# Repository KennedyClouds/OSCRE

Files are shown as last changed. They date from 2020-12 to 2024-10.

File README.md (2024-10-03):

## Documentation for the Open Snowflake Camera for Research and Education (OSCRE)

banner

Welcome to OSCRE! This platform is motivated by the need for open, affordable, and upgradeable/adaptable instrumentation to provide microphysical observations for science and educational goals. As the name implies, OSCRE was originally developed to image falling and blowing snow. Components of the system include:
* Machine vision camera + lens
* LED strobe light
* Computer
* Off-the-shelf housings mounted to a DIY wood structure
* 3D-printed parts
* Connecting cables

Within this repository, you will find all of the information needed to purchase parts and build OSCRE.  Example code to obtain images from the camera are also provided. Contributors are welcomed across all fronts ranging from hardware to software. 

## Overview of Components and Specifications

Parts, prices, and links to purchase are provided here: [Google Sheet](https://docs.google.com/spreadsheets/d/e/2PACX-1vRMlBapCWkLHQBSs0PFnScLlecqJcO5ei3qQ1w7xbT3gDOsDzhMCTewoKGWSilK1sk8NCsqLQS7hyFb/pubhtml) As of 3 October 2024, this is out of date and will be updated soon. 

## Camera and Lens

### *Camera*

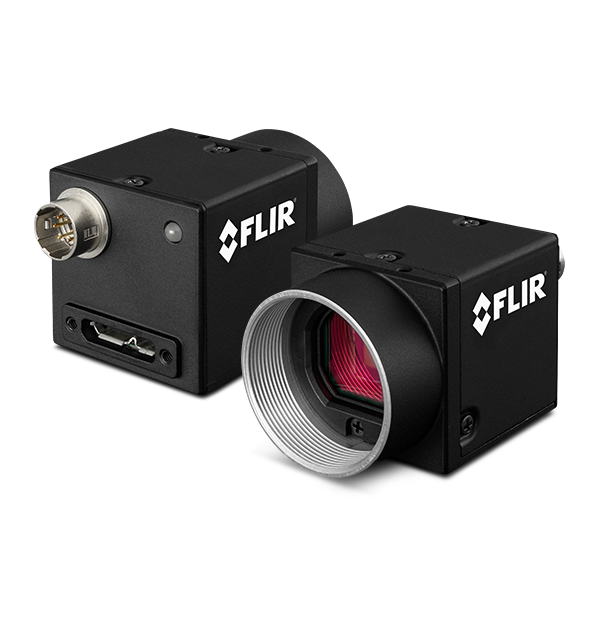
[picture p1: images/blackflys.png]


OSCRE uses a **singular** machine vision camera to obtain images of hydrometeors. These types of cameras are lightweight and rugged, making them ideal for industrial applications such as barcode scanning. A variety of manufacturers exist (Basler, FLIR, JAI, Ximea, etc.) and many of them have models that use identical image sensors from manufacturers such as Sony.

In selecting an appropriate camera/sensor, the following considerations were made:

- Affordability (<$1000 USD)
- Imaging performance (CMOS, monochrome, global shutter, noise performance)
- Minimum exposure time <= 10us (can minimize issues with lighting)
- Adequate General Purpose Input/Output (GPIO) control (this provides the signal to the LED light)
- Software compatibility with ARM architecture (Nvidia GPU computers)
- Adequate frame rate (30+fps)
- Connectivity (USB3)

A quick perusal of any of the manufacturers will yield a mind boggling number of choices. The original testbed used a JAI GO-2400M-USB 2.3MP camera, and this is a perfectly acceptable camera for obtaining images. The downside of this camera is a software SDK free for Windows, but requires an expensive (~$500) computer specific license for other architecture. Supposedly this is changing in 2021, but documentation for the 3rd party SDK is also limited.  

Instead, development shifted to FLIR for the model documented herein. The [FLIR Spinnaker SDK](https://www.flir.com/products/spinnaker-sdk/) is available for all platforms which means you could use any computer you already own to drive the system assuming the hardware is adequate. Based on the criteria above, the Blackfly S line was selected. Balancing the requirements, the [BFS-U3-32S5M-C](https://www.flir.com/products/blackfly-s-usb3/?model=BFS-U3-32S4M-C)  offered the best bang for the buck.  For ~$800, the camera uses the Sony IMX252 monochrome sensor to acquire 3.2MP images at rates up to 118fps. The smaller 1/1.8" sensor is advantageous because it offers a longer focal length for a given resolution, increasing the depth of field compared to larger sensors. 

### *Lens*

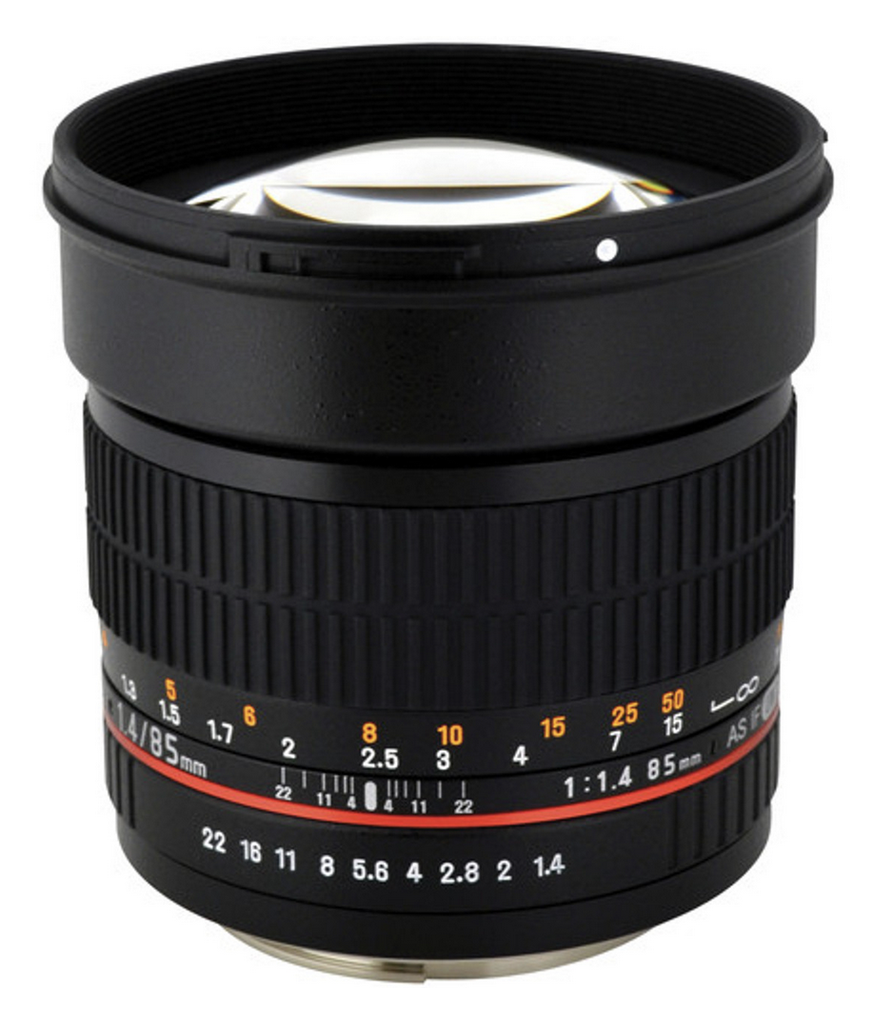
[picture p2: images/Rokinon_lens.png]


OSCRE uses a [Rokinon 85mm f1.4 lens](https://www.bhphotovideo.com/c/product/769424-REG/) with manual aperture and focus controls. This is a larger lens designed for traditional Single-Lens Reflex (SLR) cameras. Compared to many (most) machine vision camera lenses, the larger size allows the camera system to only utilize the very center of the optics yielding virtually distortion free images. In other words, a hydrometeor imaged anywhere within the frame will be identical in size. Further, there are no concerns with optical quality (resolution) if the camera is upgraded to a higher resolution sensor in the future. The Rokinon lens is available in a variety of camera mounts but parts are designed for Nikon (F) mount version. Note that the lens requires an [adapter](https://www.bhphotovideo.com/c/product/995071-REG/fotodiox_nk_c_c_mount_movie_lens_adapter.html) from the parent mount to the C-mount thread the machine vision camera provides.  

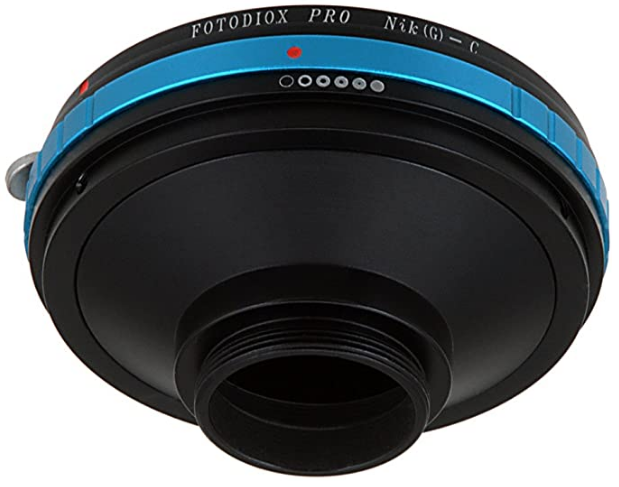
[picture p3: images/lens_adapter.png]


## Computer

OSCRE is driven by NVIDIA GPU computers. Currently, the system is designed upon the reComputers offered by [Seeed Studio](https://www.seeedstudio.com/). Parts based off the dimensions of their A206 carrier board. For a budget friendly build, the [Jetson Nano](https://www.seeedstudio.com/reComputer-J1020-v2-w-o-power-adapter-p-5608.html) can be bought for ~$300. If you would like faster processing, the [Orin Nano](https://www.seeedstudio.com/reComputer-J3010-w-o-power-adapter-p-5631.html) is a better option for ~$500. Note that 3rd party power adapters are recommended for wiring purposes. For either of these options, the computer is removed from the Seeed housing and directly mounted to the 3D printed bracket. An m.2 SSD hard drive can be added prior to mounting. A 1TB SSD should be sufficient for most applications. 

## Housings and Structure

OSCRE uses dotworkz S-Type Ring of Fire or Heater Blower Camera Enclosures (ST-RF-MVP or ST-HB-MVP-SS). These housings are waterproof and quite robust... thus far, they have survived winters in North Dakota and Colorado with no weatherproofing issues. The Ring of Fire series is suggested for coldest installs (< -10C). 

## Instructions to build OSCRE
See: [Instructions readme](https://github.com/KennedyClouds/OSCRE/blob/main/Instructions/README.md)

## 3D-printed parts
See: [3D Printing readme](https://github.com/KennedyClouds/OSCRE/blob/main/3D-prints/README.md)

## Connecting cables
See: [Cables readme](https://github.com/KennedyClouds/OSCRE/blob/main/Cables/README.md)

## Software and installation

Coming Soon! Contact me if assistance is needed prior to getting this section online. 

Shield: [][cc-by]

This work is licensed under a
[Creative Commons Attribution 4.0 International License][cc-by].

[][cc-by]

[cc-by]: http://creativecommons.org/licenses/by/4.0/
[cc-by-image]: https://i.creativecommons.org/l/by/4.0/88x31.png
[cc-by-shield]: https://img.shields.io/badge/License-CC%20BY%204.0-lightgrey.svg

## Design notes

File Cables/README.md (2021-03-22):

## Documentation for Cables

This document describes how to make the cables for OSCRE. 

## Power Cable
Tools:  diagonal cutting pliers ~$10, wire stripping tool ~$10. Razor blade knife ~$10, smaller philips or flathead screwdriver ~$5.
Supplies: One outdoor rated, 16/3 extension cable of desired length (I use 10').  Note: you may be able to find one with bare leads, but selection is usually limited. 

###### Step 1: 
Use the diagonal cutting pliers to cut off the female plug. This will exposes the three 16AWG cables.  Tip: Do not use the cutting surface of the stripping tool. This is typically too weak
to cleanly cut through the bundle. 

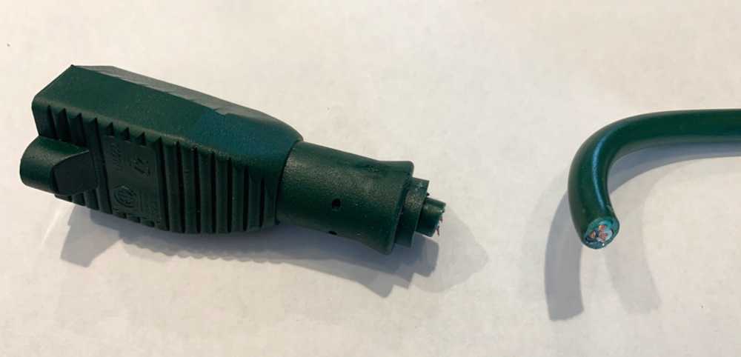
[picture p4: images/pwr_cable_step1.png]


###### Step 2: 
Use the razor blade to carefully score the outer sheathing 4-5cm from the end of the cable. Make sure you do not cut into the inner wires! Once the wire is scored, the outer vinyl should slide off with a pull. 
Next, use the 16AWG notch to strip ~1cm of each inner cable.  The inner wire is most likely braided vs. solid copper. Gently twist the copper ends to limit fraying. 

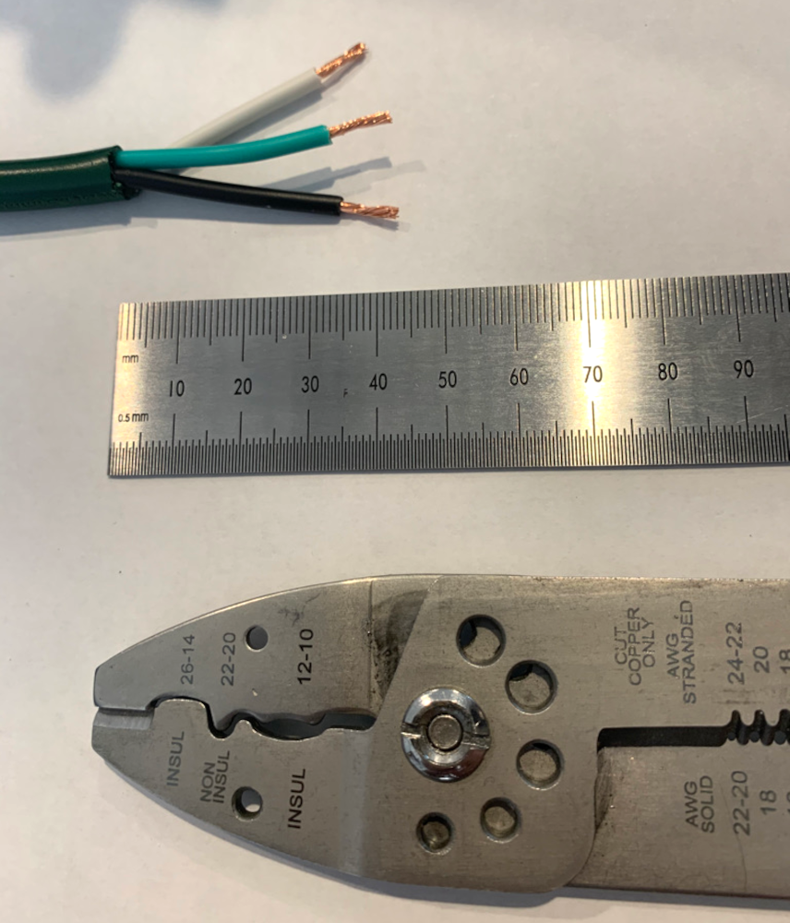
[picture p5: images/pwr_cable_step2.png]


###### Step 3: 
Loosen the weatherproof plug on the underside of the housing and insert the cable. Make sure the threaded piece is still on the cable so you can secure it later. 

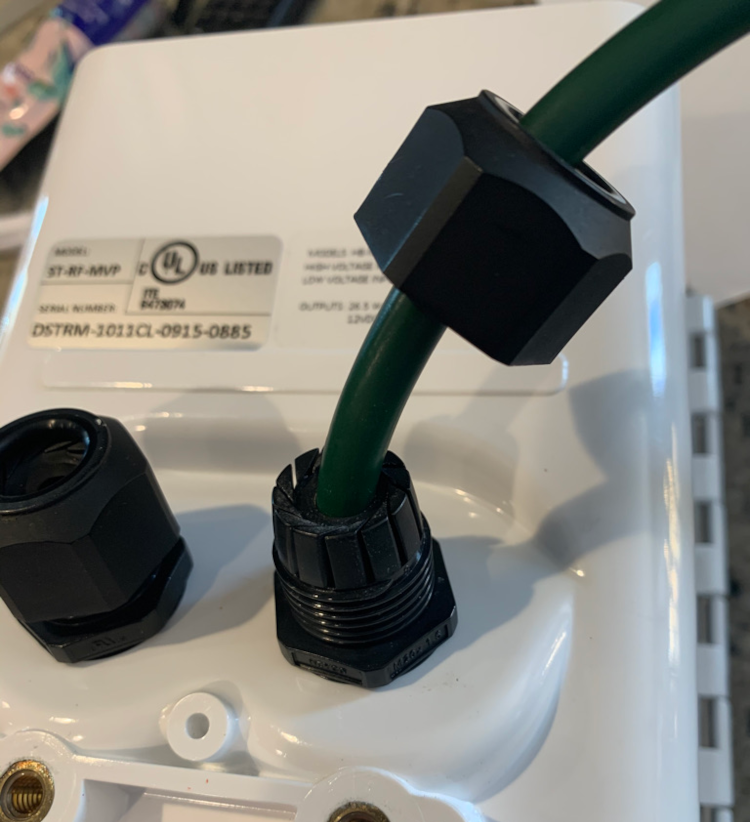
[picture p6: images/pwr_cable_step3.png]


###### Step 4: 
Use the screwdriver to loosen the connections on the power supply. Match colors (green = ground, black = hot, white = neutral), insert, then tighten the screws to secure. 
You should not see exposed copper wire. Once secure, make sure there is adequate slack (see picture), then tighten the fitting to secure the cable.  

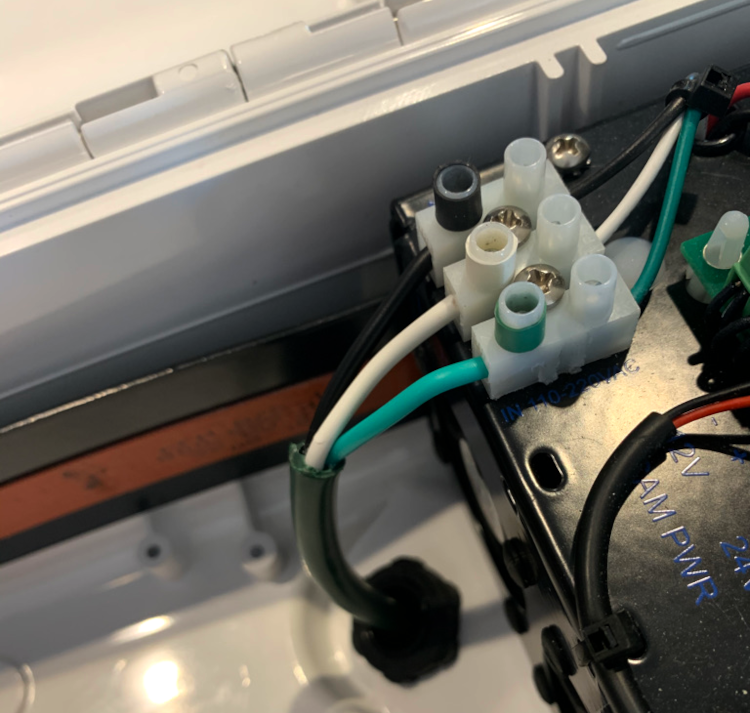
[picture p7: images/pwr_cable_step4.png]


## Lighting Cable

Shield: [][cc-by]

This work is licensed under a
[Creative Commons Attribution 4.0 International License][cc-by].

[][cc-by]

[cc-by]: http://creativecommons.org/licenses/by/4.0/
[cc-by-image]: https://i.creativecommons.org/l/by/4.0/88x31.png
[cc-by-shield]: https://img.shields.io/badge/License-CC%20BY%204.0-lightgrey.svg

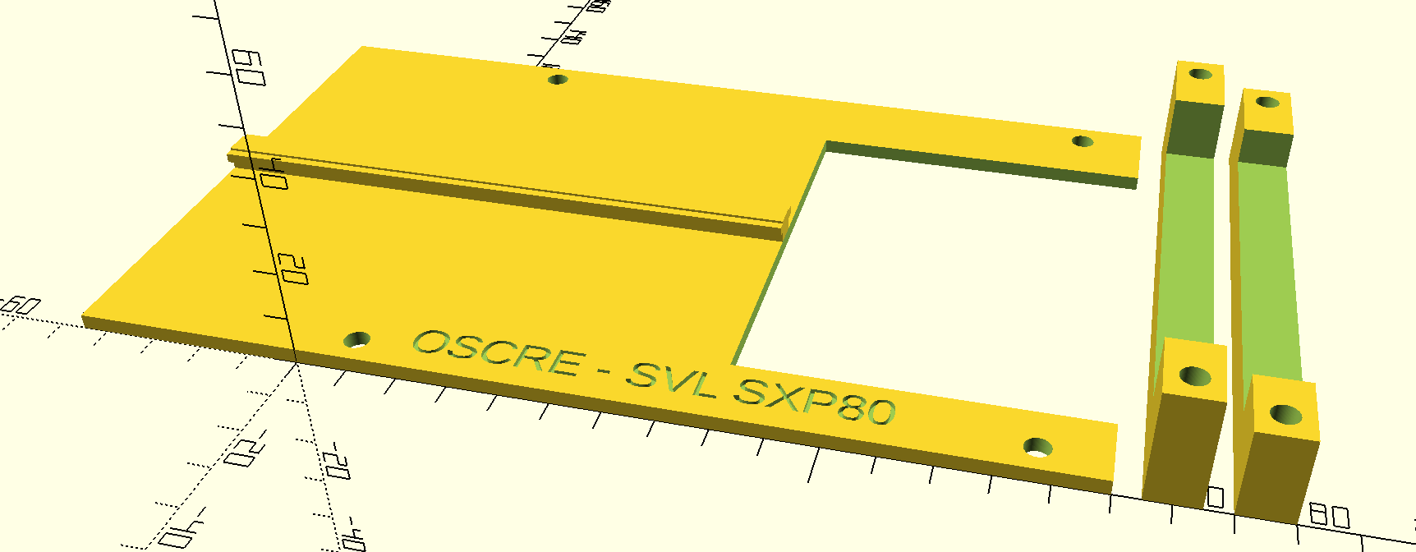
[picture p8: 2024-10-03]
images/OSCRE_SXP80_mount.png

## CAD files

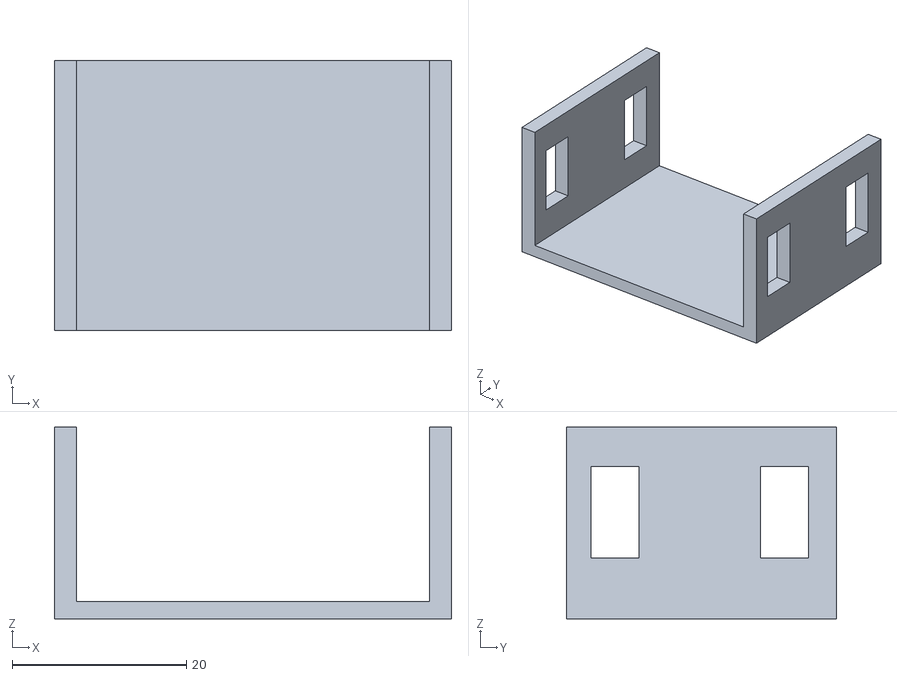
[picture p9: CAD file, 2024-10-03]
3D-prints/OSCRE_FLIR_clip.stl
45.6 x 31.0 x 22.0

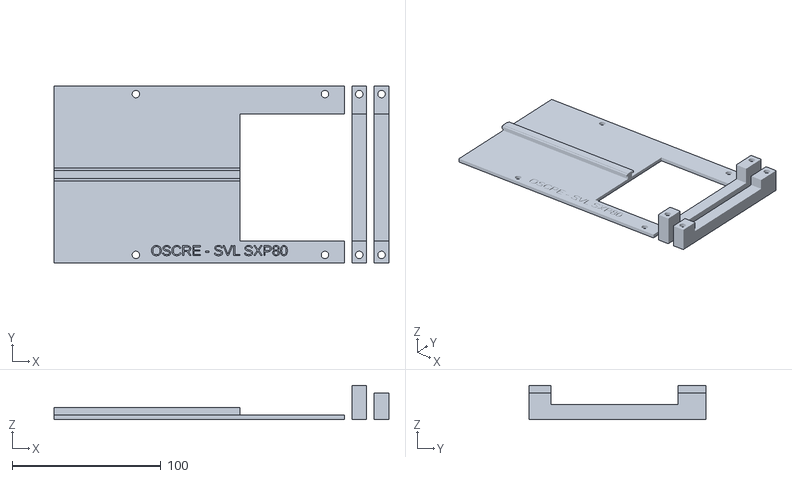
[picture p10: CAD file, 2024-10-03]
3D-prints/OSCRE_SXP80_mount.stl
225.0 x 119.0 x 23.0

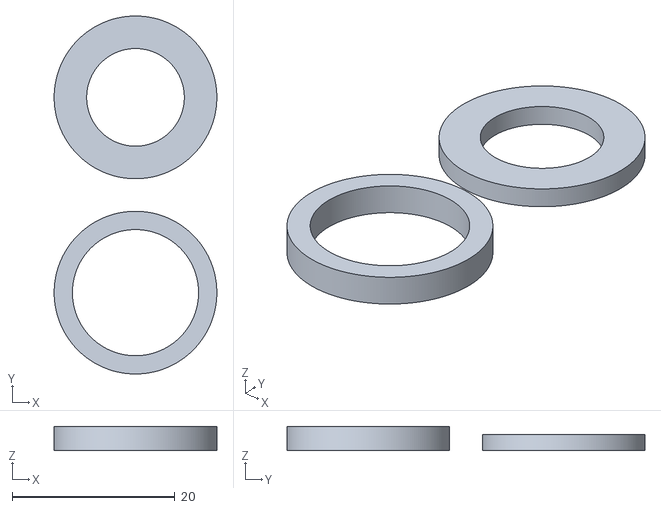
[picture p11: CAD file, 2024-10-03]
3D-prints/OSCRE_SXP80_cable_adapters.stl
20.0 x 44.0 x 3.00

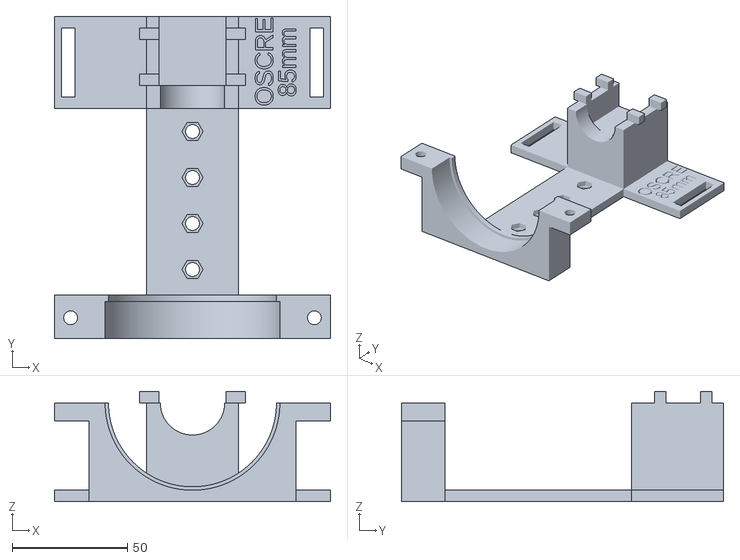
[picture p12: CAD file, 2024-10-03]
3D-prints/OSCRE_lens-cam_mount_plate.stl
120.0 x 140.0 x 48.0

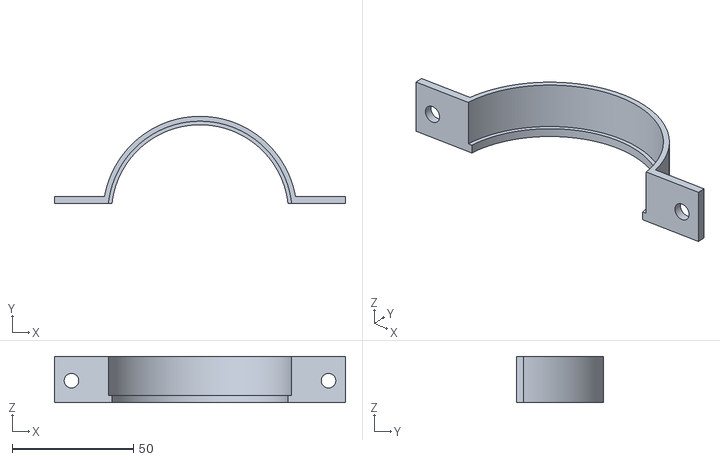
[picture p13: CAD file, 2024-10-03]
3D-prints/OSCRE_lens_top_plate.stl
120.0 x 36.0 x 19.0

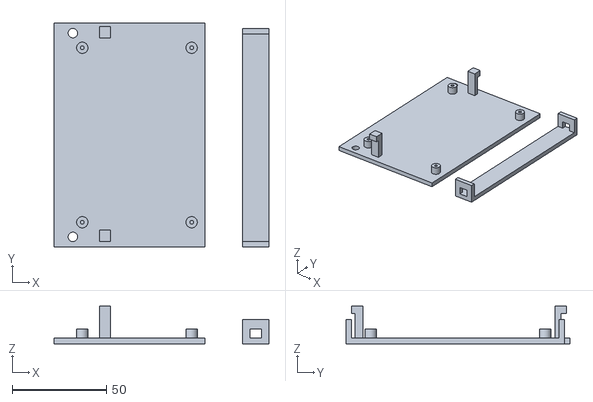
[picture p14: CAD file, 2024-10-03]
3D-prints/OSCRE_computer_mount.stl
114.0 x 119.0 x 20.0

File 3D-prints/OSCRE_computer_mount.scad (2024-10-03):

//OSCRE Seeed A206 Jetson board mount
//https://github.com/KennedyClouds/OSCRE
//1 October 2024 - Aaron Kennedy - aaron.kennedy@und.edu
wb=119/2.;
th=3; // thickness
$fn = 200*1;
 difference() {
        union() {
            //base
            color("green") cube([80,119,th]); //length, width, height
            
            //clip connects
            color("green") translate([24,3,0]) cube([6,6,th+17]); //length, width, height
            color("green") translate([24,111,0]) cube([6,6,th+17]); //length, width, height
            
            //mounting posts
            color("green") translate([10+5,13.25,0]) cylinder(h=th+5,r = 3);
            color("green") translate([10+5+58,13.25+92.5,0]) cylinder(h=th+5,r = 3);
            color("green") translate([10+5+58,13.25,0]) cylinder(h=th+5,r = 3);
            color("green") translate([10+5,13.25+92.5,0]) cylinder(h=th+5,r = 3);   
            
            //clip
            color("green") translate([100,0,0]) cube([14,116,th]); //length, width, height
            color("green") translate([100,0,0]) cube([14,3,th+10]); //length, width, height
            color("green") translate([100,113,0]) cube([14,3,th+10]); //length, width, height
            }   

        //Cut-outs 
        //Threaded hole for bottom pieces  
        color("pink") translate([10,wb*2-5.5,-1]) cylinder(h=th+2,r = 2.5);   
        color("pink") translate([10,5.5,-1]) cylinder(h=th+2,r = 2.5);
        color("pink") translate([10+5,13.25,3]) cylinder(h=th+5,r = 1);
        color("pink") translate([10+5+58,13.25+92.5,3]) cylinder(h=th+5,r = 1);
        color("pink") translate([10+5+58,13.25,3]) cylinder(h=th+5,r = 1);
        color("pink") translate([10+5,13.25+92.5,3]) cylinder(h=th+5,r = 1);
            
        //clip connectors    
        color("white") translate([24,2,th]) cube([6,3,13]); //length, width, height
        color("white") translate([24,114,th]) cube([6,3,13]); //length, width, height
     
        //clip    
        color("white") translate([104,0,th]) cube([6,3,5]); //length, width, height
        color("white") translate([104,113,th]) cube([6,3,5]); //length, width, height    
            
 }

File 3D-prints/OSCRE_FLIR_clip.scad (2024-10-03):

//OSCRE FLIR camera clip v1.0
//1 October 2024 - Aaron Kennedy - aaron.kennedy@und.edu
include <cyl_head_bolt.scad>;
$fn = 200 *1; //Ensure 
 difference() {
        union() {
            //base
            color("green") cube([45.6,31,22]); //length, width, height           
            }
            color("pink") translate([0,2.8,7])cube([45.6,5.5,10.5]); //length, width, height
            color("pink") translate([0,22.3,7])cube([45.6,5.5,10.5]); //length, width, height
            color("white") translate([2.5,0,2])cube([40.6,31,20]); //length, width, height
             
 }
 

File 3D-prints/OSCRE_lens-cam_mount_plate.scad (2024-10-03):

//OSCRE Rokinon 85mm / FLIR camera bottom plate v1.0
//https://github.com/KennedyClouds/OSCRE
//1 October 2024 - Aaron Kennedy - aaron.kennedy@und.edu
//Includes functions from https://github.com/JohK/nutsnbolts 
include <cyl_head_bolt.scad>;

$fn = 200*1; //Ensures adequate facets for circular parts
 difference() {
        union() {
            //base
            color("green") cube([120,140,76/2.+5]); //length, width, height
            color("green") translate([37,110,76/2.+5])cube([46,5,5]); //length, width, height
            color("green") translate([37,130,76/2.+5])cube([46,5,5]); //length, width, height
            
            }
            //Cut outs for lens
            color("darkgreen") rotate([90,0,0]) translate([60,76/2.+5,-16]) cylinder(h=16,r = 76/2.);
            color("darkgreen") rotate([90,0,0]) translate([60,73/2.+6.5,-19]) cylinder(h=3,r = 73/2.);
            color("blue") translate([0,19,5]) cube([120,100-19,76/2.+5]); //length, width, height
            //Cut outs for lens mount
            color("blue") translate([0,0,0]) cube([15,19,35]); //length, width, height
            color("blue") translate([0,19,0]) cube([40,81,5]); //length, width, height
            color("blue") translate([105,0,0]) cube([15,19,35]); //length, width, height
            color("blue") translate([80,19,0]) cube([40,81,5]); //length, width, height
            
            
            //Additional cuts
            color("blue") translate([45.5,110,28]) cube([29,50,30]); //length, width, height
            color("red") rotate([90,0,0]) translate([60,76/2.+5,-110]) cylinder(h=10,r = 28/2.);
            color("blue") translate([0,100-19,5]) cube([40,60,76/2.]); //length, width, height           
            color("blue") translate([80,100-19,5]) cube([40,60,76/2.]); //length, width, height
       
            //Mounting holes
            color("darkgreen") translate([60,30,0]) cylinder(h=5,r = 3);
            color("darkgreen") translate([60,50,0]) cylinder(h=5,r = 3);
            color("darkgreen") translate([60,70,0]) cylinder(h=5,r = 3);
            color("darkgreen") translate([60,90,0]) cylinder(h=5,r = 3);
            translate([60,30,2]) rotate([180,0,0]) nutcatch_parallel("M5", clh=0.1);
            translate([60,50,2]) rotate([180,0,0]) nutcatch_parallel("M5", clh=0.1);
            translate([60,70,2]) rotate([180,0,0]) nutcatch_parallel("M5", clh=0.1);
            translate([60,90,2]) rotate([180,0,0]) nutcatch_parallel("M5", clh=0.1);
            
            color("blue") translate([111,105,0]) cube([6,30,5]); //length, width, height
            color("blue") translate([3,105,0]) cube([6,30,5]); //length, width, height
            //holes for lens mount
            color("darkgreen") translate([7,9,30]) cylinder(h=15,r = 3);
            color("darkgreen") translate([113,9,30]) cylinder(h=15,r = 3);
            translate([7,9,35]) rotate([180,0,0]) nutcatch_parallel("M5", clh=0.1);
            translate([113,9,35]) rotate([180,0,0]) nutcatch_parallel("M5", clh=0.1);
            
            
            color("pink") rotate([0,0,90]) translate([101,-95,2]) linear_extrude(height = 3)     text("OSCRE",size=8);
            color("pink") rotate([0,0,90]) translate([105,-105,2]) linear_extrude(height = 3)     text("85mm",size=8);  
 }
 

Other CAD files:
3D-prints/OSCRE_lens_top_plate.scad
3D-prints/OSCRE_SXP80_cable_adapters.scad
3D-prints/OSCRE_SXP80_mount.scad

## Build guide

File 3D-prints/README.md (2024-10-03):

## Documentation for 3D Printing OSCRE components

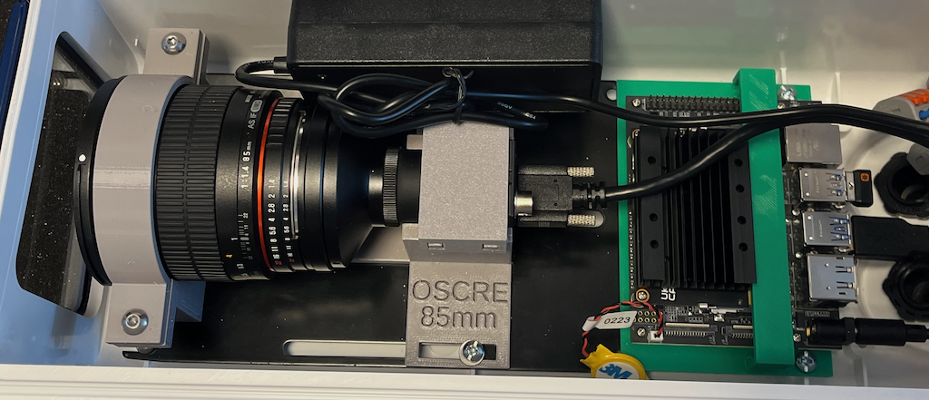
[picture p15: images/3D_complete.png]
banner


Within this directory you will find files that will allow you to print the lens and computer mounts. Files are provided in both [openSCAD](https://www.openscad.org/) and \ STL formats. These should place nice with any slicer of your choosing. 

## Overview of parts

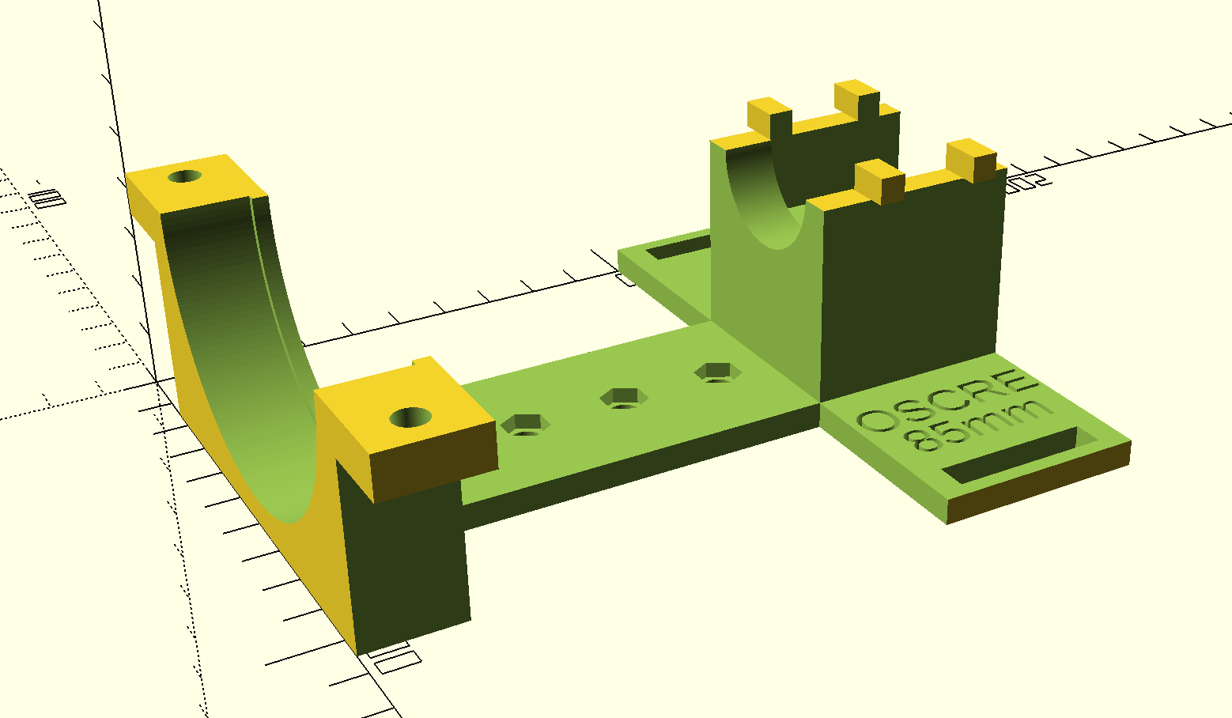
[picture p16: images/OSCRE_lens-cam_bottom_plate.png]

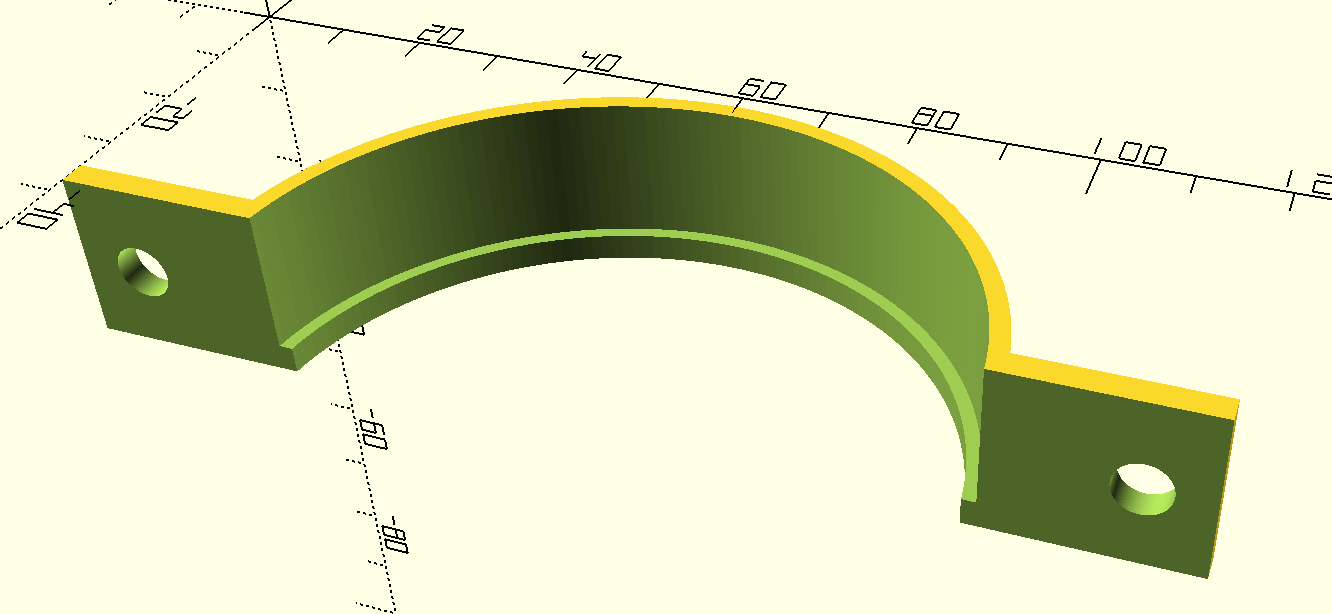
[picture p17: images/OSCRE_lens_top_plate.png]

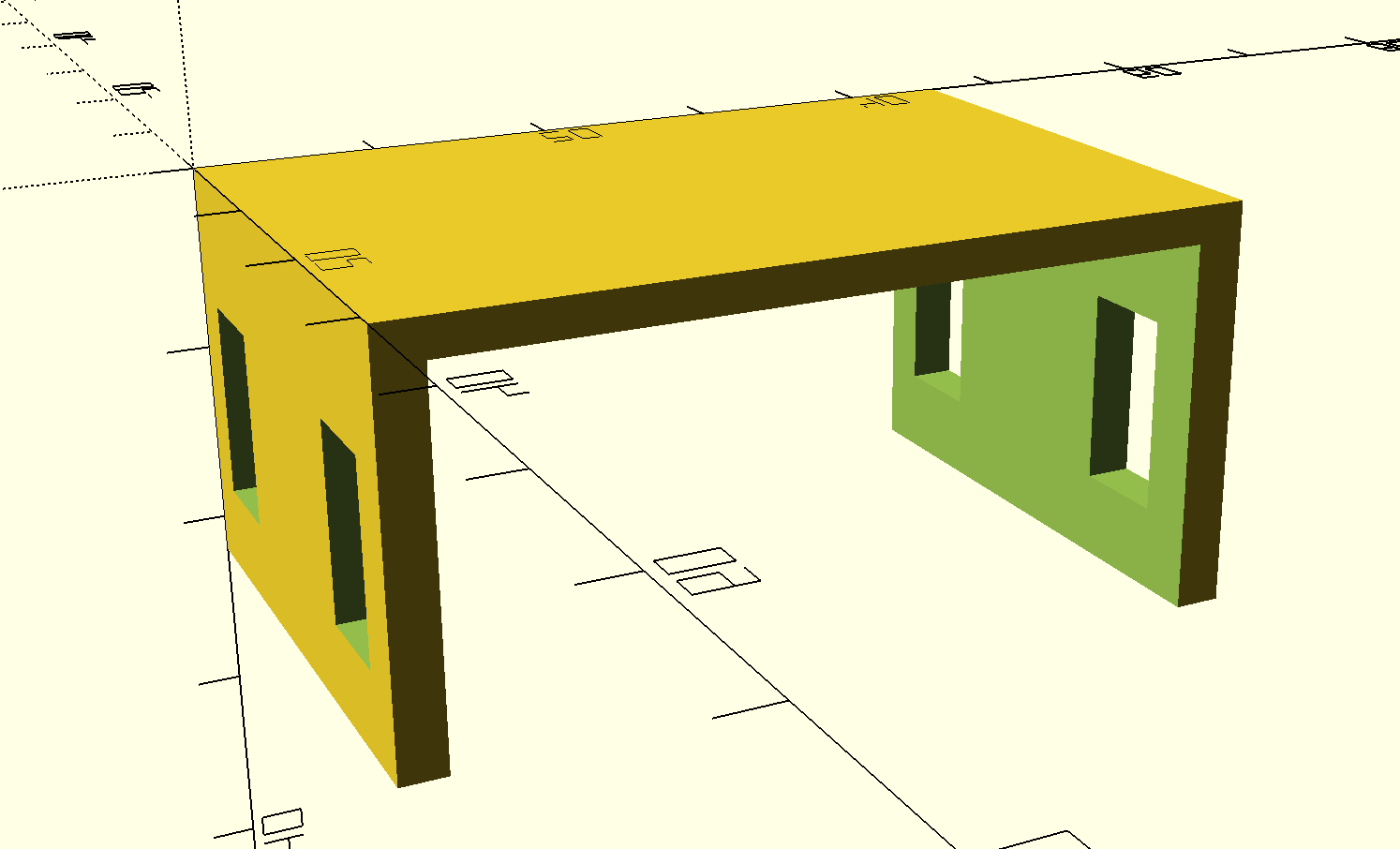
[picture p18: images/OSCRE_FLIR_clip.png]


The lensholder is designed to fit 5mm hardware. The bottom plate is first bolted to the metal plate of the Dotworkz platform. The lens and adapter is then attached to the camera and the 5mm extension tube. This is then set into the bottom plate and secured by bolting the top plate and adding the clip over the camera. Note that Dotworkz platforms sometimes have different length build plates depending on the model purchased. Exact positions may vary slightly and washers my be needed to securerly fasten to the metal plate. The front of the lens should be ~1.5cm distant from the front of the housing. 

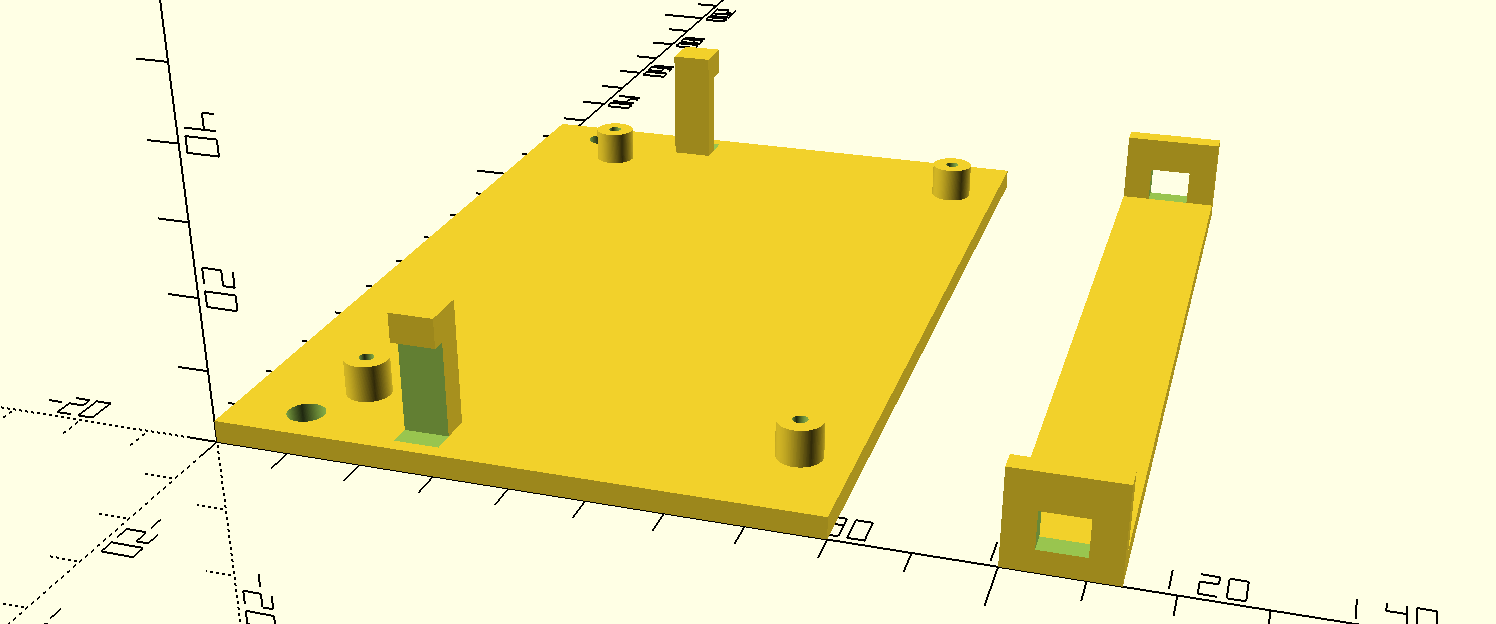
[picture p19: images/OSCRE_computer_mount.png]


The computer should first be attached to the mount. An additional clip is provided for additional security. The platform is secured with #8 screws to the predrilled holes in the DotWorkz housing.  

## Tips and Tricks for Printing

* Prints have been made on Creality Ender3 and Prusa MK3+ printers. PETG or PLA can be used (I prefer PETG).
* Make sure to use build supports. These can be carefully broken away or trimmed off after printing. 

Shield: [][cc-by]

This work is licensed under a
[Creative Commons Attribution 4.0 International License][cc-by].

[][cc-by]

[cc-by]: http://creativecommons.org/licenses/by/4.0/
[cc-by-image]: https://i.creativecommons.org/l/by/4.0/88x31.png
[cc-by-shield]: https://img.shields.io/badge/License-CC%20BY%204.0-lightgrey.svg

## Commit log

2020-12-29 OSCRE 3D printed parts
    Initial commit of parts. Includes the lens holder, the computer platform, and clip to hold computer down.
    [OSCRE_JetsonNX_Clip.scad, OSCRE_JetsonNX_Clip.stl, OSCRE_JetsonNX_platform.scad, OSCRE_JetsonNX_platform.stl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]
2021-01-04 Added 3D printing documentation
2021-03-22 Power cable updated
    Instructions and pictures for power cable assemble created.
2021-03-25 Updated platform
    Includes gap for power/reset/LED cables
    [OSCRE_JetsonNX_platform.scad, OSCRE_JetsonNX_platform.stl]
2021-04-02 Software addition
    Added sample Python code to read FLIR raw file.
2021-07-27 Added info about computer and housings
2022-09-12 85mm adapter / light bracket
    Added adapter for Rokinon 85mm lens and for the SVL ODSX30 LED light
    [OSCRE_Lens_85mm_adapter.scad, OSCRE_Lens_85mm_adapter.stl, OSCRE_ODSX30_bracket.scad]
2022-09-12 85mm lens addition
    Added details about 85mm lens option
2024-10-03 Updated 3d printed parts
    Updated 3d printed parts for OSCRE. Standardized 5mm bolts for lens, Can use #8 screws for mounting to enclosure.
    [OSCRE_FLIR_clip.scad, OSCRE_FLIR_clip.stl, OSCRE_JetsonNX_Clip.scad, OSCRE_JetsonNX_Clip.stl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]
2024-10-03 Create 3D_complete.png
    added file of 3d prints in camera housing

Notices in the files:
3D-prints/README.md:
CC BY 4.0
